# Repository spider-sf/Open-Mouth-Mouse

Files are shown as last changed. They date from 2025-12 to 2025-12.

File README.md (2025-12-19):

# Open-Mouth-Mouse 

An open-source, affordable assistive technology project that enables computer control through mouth movements and sip/puff actions. This is an updated version of the original Mouth-Operated Mouse, that has been toughened up with a custom pcb and more robust case in order to be deployed for daily use by tetraplegics. This project was developed for the ParaWork team at the Swiss Paraplegic Centre in order to enable quick access to this type of assistive device, bypassing the need to involve insurance companies.

## Overview

This project creates a mouth-operated mouse combining a pressure sensor for sip/puff actions with a joystick for cursor movement, allowing users with limited hand mobility to control a computer. A keyboard mode is also included, where 2 to 8 keybinds are assigned to different angles, and special keys can be bound to sips and puffs. The mouse functions as follows:

*   **Joystick**: Controls cursor movement (operated by mouth)
*   **Sip/Puff Actions**: 
    *   Hard puff → Right click
    *   Soft puff → Scroll down
    *   Neutral → No action
    *   Soft sip → Scroll up
    *   Hard sip → Left click
These controls are inverted from the previous version because users requested it.

## Upgrades over the main V3

*   **Custom PCB**: The circuit now no longer needs to be completely hand soldered, only the components need to be attached.
*   **Improved case**: The case is now more robust and has a pressed in 1/4 nut to allow for attaching to standard camera mounts.

## Components

1.  **Arduino pro micro** (~$1 USD)
    *   Replaces Arduino Uno and Leonardo for direct HID capabilities and a more compact design.
    *   Pinout must match the SparkFun Electronics version in order to fit in PCB, there are many on aliexpress that fit this requirement.
2. **Custom PCB** (~$1 USD per board + $5-$20 shipping
    *   Hand the gerber files to one of the large manufacturers, the total price per delivered pcb obviously goes down as you order more, so consider doing a batch production.
3.  **NPA-500B-001G** (~$30 USD)
    *    - Specifically designed for sip/puff applications
         - I have tested another sensor but it didn't behave similarly to the NPA sensor, more testing needed to find the correct affordable version. This is where the most improvement in price can still be found.
4.  **PS4 Thumb Joystick** (~$1 USD)
    *   The PCB fits a PS4 thumb joystick, ideally choose a TMR magnetic version to allow for more precision and setting a smaller deadzone.
5.  **Tubing** (~$1 USD)
    *   Food-grade silicone tubing 1 meter - 2mm x 3mm 
6.  **3d Printed parts**
    *   Mouthpeice and Casing (Cost varies, ideally the maker has their own printer or access to one)
7.  **Soldering Components:**
    *   Basic soldering stuff, solder, flux (fluxed solder works too, make sure you have a fine tip)
    *   USB to USB-C cable for Arduino (~$1 USD)
    *   1uf electrolytic capacitor (~$0.1 USD)
8. **Small M3 Screws**
    *   Just some short m3 screws of any type
    
**Estimated Total Cost:** Approximately $40 USD not including shipping, cost varies from country to country and quantity of parts ordered.

## Setup Instructions

### 1. PCB Assembly

Follow this order for soldering to the board:

*   **Pressure sensor**
    *   Start with this as it will be difficult once the other components are attached.
    *   Follow [this tutorial](https://youtu.be/EW9Y8rDm4kE?si=filJ9XeB6xgZvDsz&t=374) to solder the pressure sensor, this is the trickiest part to do, just be patient and it will be fine.
    *   Dont forget to check that the orientation of the chip is correct by matching the dot in the corner to the one on the pcb.
    *   Even if only 3 pins are necessary for the sensor to function, you should still solder all of the pins otherwise it will be too weakly attached.
*   **Through hole components**
    *   Now you can solder all of the other components to the board, the order is not important. As they are all through-hole components the technique for doing so is the same for all of them [here is a tutorial](https://youtu.be/vAx89WhpZ3k?si=IwgAvfRAVOeoopeO) if you are unsure.
    *   Remember to connect the capacitor with correct polarity.

### 2. Arduino IDE Setup

1.  **Install Arduino IDE**: Download and install the Arduino IDE from the [official website](https://www.arduino.cc/en/software).
2.  **Install Arduino Pro Micro Board**: Go to `Tools > Board > Boards Manager...` and search for "Arduino AVR Boards". Install the package that includes the Arduino Leonardo.
3.  **Install Libraries**: The `V3.ino` sketch uses the built-in `Mouse.h` library. No additional library installations are required for the Arduino sketch.
4.  **Upload Sketch**: Open `V3.ino` in the Arduino IDE, select `Tools > Board > Arduino Pro Micro`, and choose the correct `Port`. Then, click `Upload`.

### 3. Case Assembly

*   **Lower Casing**
    *   Press the 1/4 nut into the hole in the lower casing, it should be set deep enough that the screw on whatever arm you are using can grab onto it.
    *   Place the PCB inside of the case with the joystick sitting above the nut.
    *   Fasten the PCB in place with 4 short m3 screws.
*   **Mouthpiece**
    *   Cut a piece of the silicon food-grade tubing about 10 cm long.
    *   Connect the tubing to the pressure port on the sensor, there are 2 pressure ports for most models, the one closer to the dot in the corner should be the one you connect to, the other one inverts sips and puffs.
    *   The other end of the tubing connects to the hole on the mouthpiece.
    *   Place the mouthpiece on the joystick.
    *   At this poimt the mouse should already be functional, plug it in and try it out to check. If not do the troubleshooting now before you close it up.
*   **Upper Casing**
    *   Temporarily remove the tube from the mouthpiece.
    *   Thread your tubing through the small hole on the top half of the casing.
    *   Then place the top case ontop of the lower and press it down.
    *   Fasten the parts together with 4 more m3 screws.
    *   Reattach the tube to the mouthpiece.

### 3. Python Application Setup

1.  **Install Python**: Ensure you have Python 3.x installed. You can download it from [python.org](https://www.python.org/downloads/).
2.  **Install Dependencies**: Open a terminal or command prompt and navigate to the directory where `App.py` is located. Install the required Python libraries using pip:
    ```bash
    pip install pyserial customtkinter pyautogui
    ```
3.  **Run Application**: Execute the Python application:
    ```bash
    python App.py
    ```
## Usage

Once the Arduino sketch is uploaded and the Python application is running, you can use the `App.py` interface to:

*   **Connect to Arduino**: Select the serial port connected to your Arduino Leonardo and click "Connect".
*   **Tune Parameters**: Adjust the pressure thresholds (Hard Sip, Neutral Min/Max, Soft Puff, Hard Puff) and joystick deadzone/cursor speed. Apply settings to the Arduino.
*   **Calibrate Sensor**: Use the "Calibrate Sensor" tab to visualize real-time pressure readings and fine-tune your thresholds for optimal performance.
*   **Train**: Utilize the "Trainer" tab to practice and improve your control.
*   **Manage Profiles**: Save and load different configurations as profiles.

## Troubleshooting

*   **Arduino Not Detected**: Ensure the Arduino Pro Micro drivers are correctly installed and the correct port is selected in the Arduino IDE and `App.py`.
*   **Serial Communication Issues**: Verify that no other application is using the serial port. Restarting the Arduino IDE or `App.py` might help.
*   **Mouse Not Moving/Clicking**: Check the pressure sensor and joystick connections. Ensure the `V3.ino` sketch is successfully uploaded to the Arduino Leonardo.
*   **Calibration**: The pressure thresholds are highly dependent on your specific sensor and lung capacity. Use the "Calibrate Sensor" tab in `App.py` to find your optimal settings.

## Link for video guide:

* Software: https://youtu.be/A-l-xfMGubU

## 🛠️ OSHWA Certification

This hardware project is certified by the [Open Source Hardware Association (OSHWA)](https://www.oshwa.org/).

**Certification UID**: [AU000021](https://certification.oshwa.org/au000021.html)
## Contributing

Contributions are welcome! Please feel free to fork the repository, make improvements, and submit pull requests. For major changes, please open an issue first to discuss what you would like to change.

## License

This project is open-source and available under the [MIT License](https://opensource.org/licenses/MIT).

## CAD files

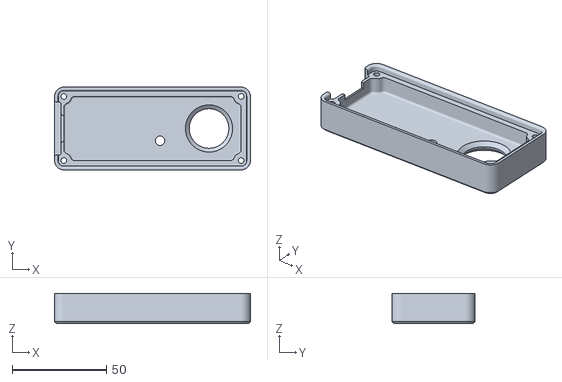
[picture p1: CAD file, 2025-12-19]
caseUpper.stl
104.0 x 44.0 x 16.0

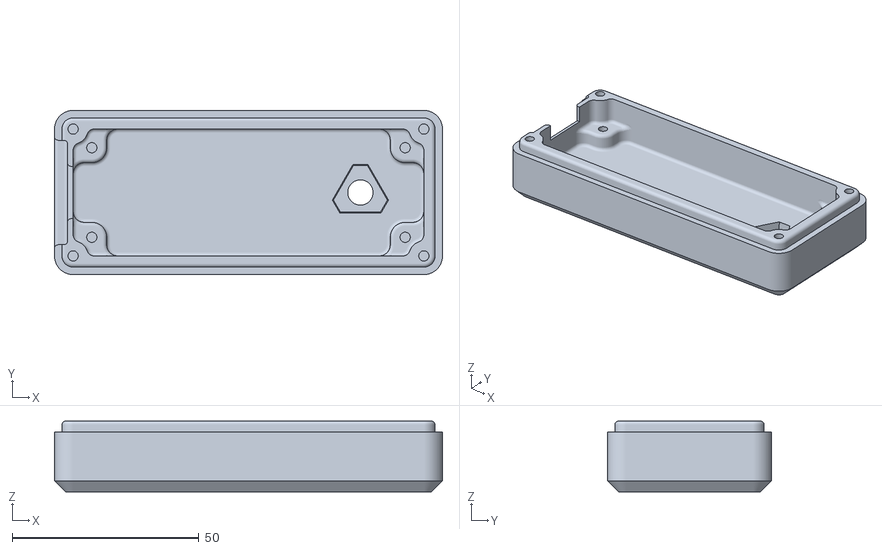
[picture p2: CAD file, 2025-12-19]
caseLower.stl
104.0 x 44.0 x 19.0

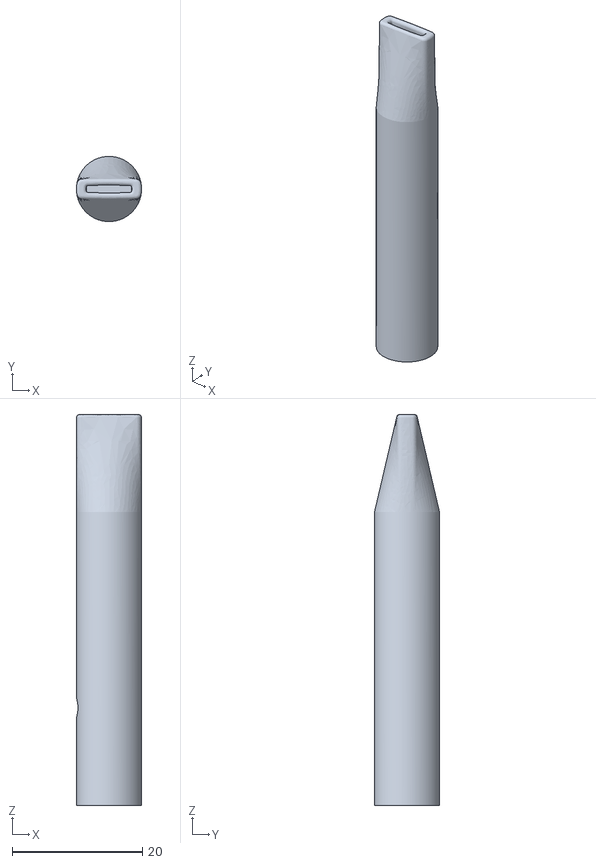
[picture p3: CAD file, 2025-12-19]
mouthpiece.stl
10.0 x 10.00 x 60.0
